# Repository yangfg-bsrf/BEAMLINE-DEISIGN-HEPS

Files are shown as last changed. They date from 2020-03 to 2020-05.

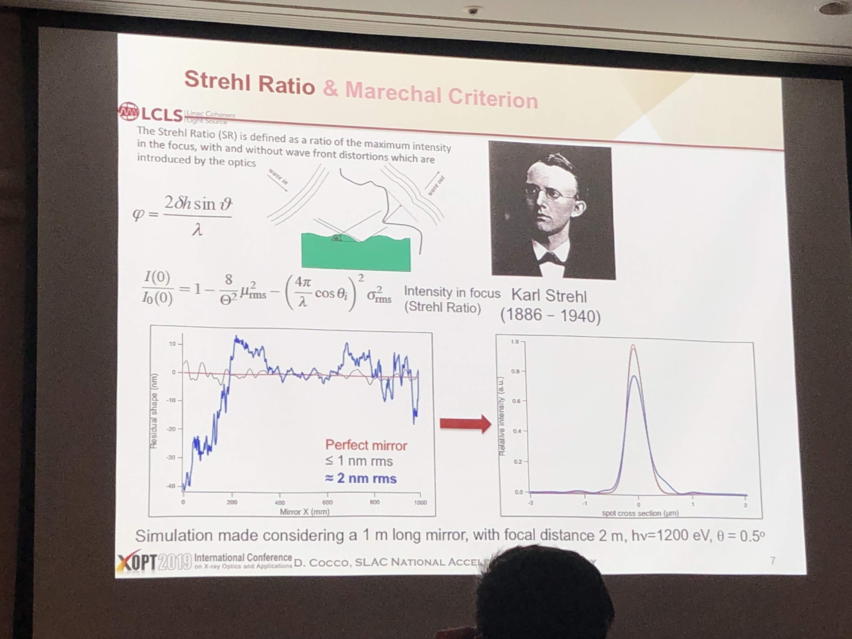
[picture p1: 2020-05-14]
report_discussion/反射镜面形误差2020-4-11/Coco/IMG_3269.JPG

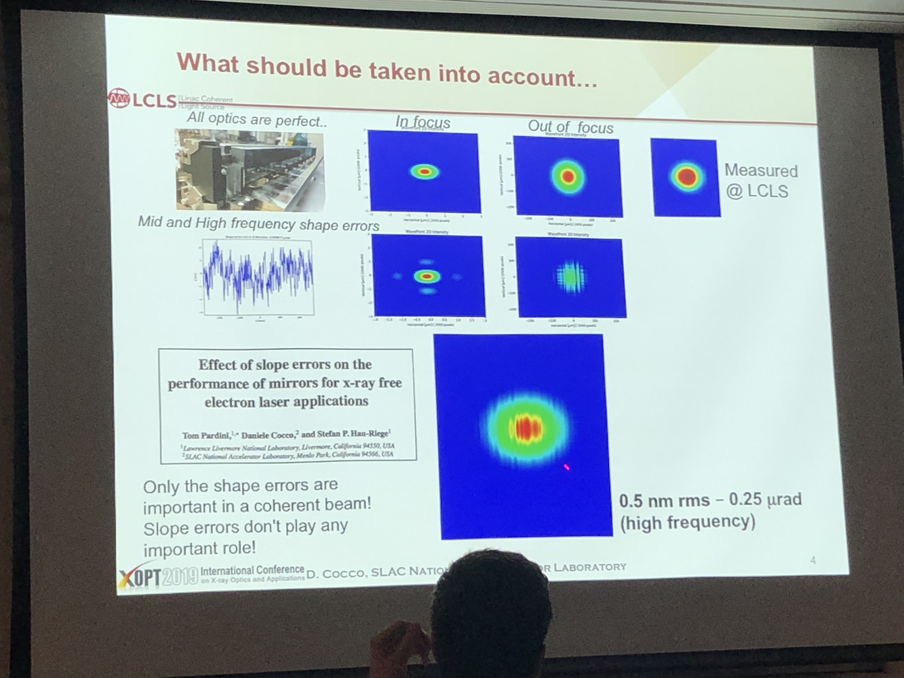
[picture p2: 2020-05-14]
report_discussion/反射镜面形误差2020-4-11/Coco/IMG_3266.JPG

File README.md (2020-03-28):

# BEAMLINE DEISIGN related simulation and study@HEPS

This work relates to the beamline design work in High Energy Photon Source project since 2018.

Different simulation software, including SRW, XRT, SHADOW-OUI, SHADOW-Hybrid, are used in the different beamline performance estimation. They give us big help in the beamline design research. We appreciate the software developer's contribution.

In this project, we will include some data\examples\problems for the people who want to do related work in HEPS.  

## how to design the beamline and simulation experiment

   (1) for specific issue, simulation and theoretical study are carried out and summarized;

   (2) for specific beamline, series of simulation and study are done

## how to program

   (1) Examples for HEPS beamlines

   (2) Examples for data_analysis

   (3) Codes for specific function, such as error generation(from Ansys, metrology), optical module with error, analysis module and so on

## other resources

   (1) HEPS parameters

   (2) Database for different kind of error

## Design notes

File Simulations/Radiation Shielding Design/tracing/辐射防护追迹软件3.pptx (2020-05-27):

## B8辐射防护追迹

- 2020-5-27

## 计算条件：

- 光源
- 白光狭缝位置35.3m
- CCM单色器位置40.8m，gap 7mm，高差12.7mm
- DCM单色器位置42.85m，高差19mm
- 准直器位置 （见图，纵坐标单位mm，横坐标单位m）
前端
束线

APS 7GeV 设计准则
L
3倍Moliere半径
铅：12~15mm，取50mm
钨：8~10mm，取35mm
t
20倍辐射长度
铅：5.6mm，取300mm
钨：3.5mm，取180mm
O
重叠6.5mm

## 做图示例说明

做图比例：88:1

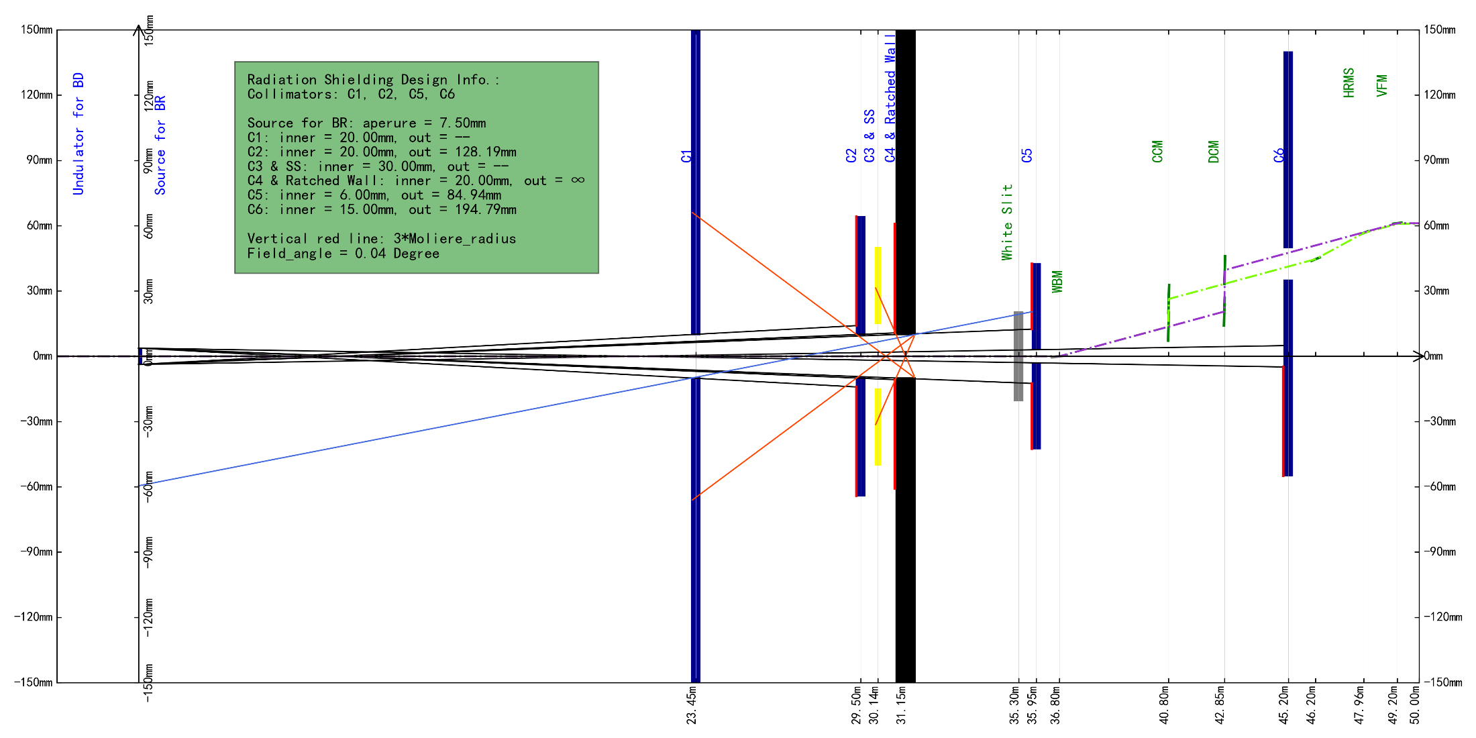
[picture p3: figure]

2. 画图比例：水平坐标m，竖直轴坐标mm
3. 各器件的位置，见对应的横纵坐标。如需光学器件的参数，后期可附

5. 器件名称：蓝色准直器件，绿色同步光学器件；全称见下。

1、包括准直器的内径，考虑3倍Moliere半径的外口径；经与石泓讨论，最终外口径可以按照10去整。

4. 光束线布局线，该束线有两个模式要考虑，因此有两条线。

器件全称名称：
White Slit:白光狭缝；WBM：白光镜；CCM：Channel-Cut晶体单色器；DCM：双晶单色器，HRMS：谐波抑制镜组；VFM：垂直聚焦镜

## B8辐射防护追迹1 -垂直方向：C5真空内 30mm

工况1
C5真空内，6mm；CCM gap =7mm, DCM offset =19mm; HRMs gap = 3mm

40.75mm
35mm
4.83mm

位置 内径 外径

C5: 35.95m, 6mm, 90mm
C6: 45.2m, 15mm, 200mm

## 水平方向

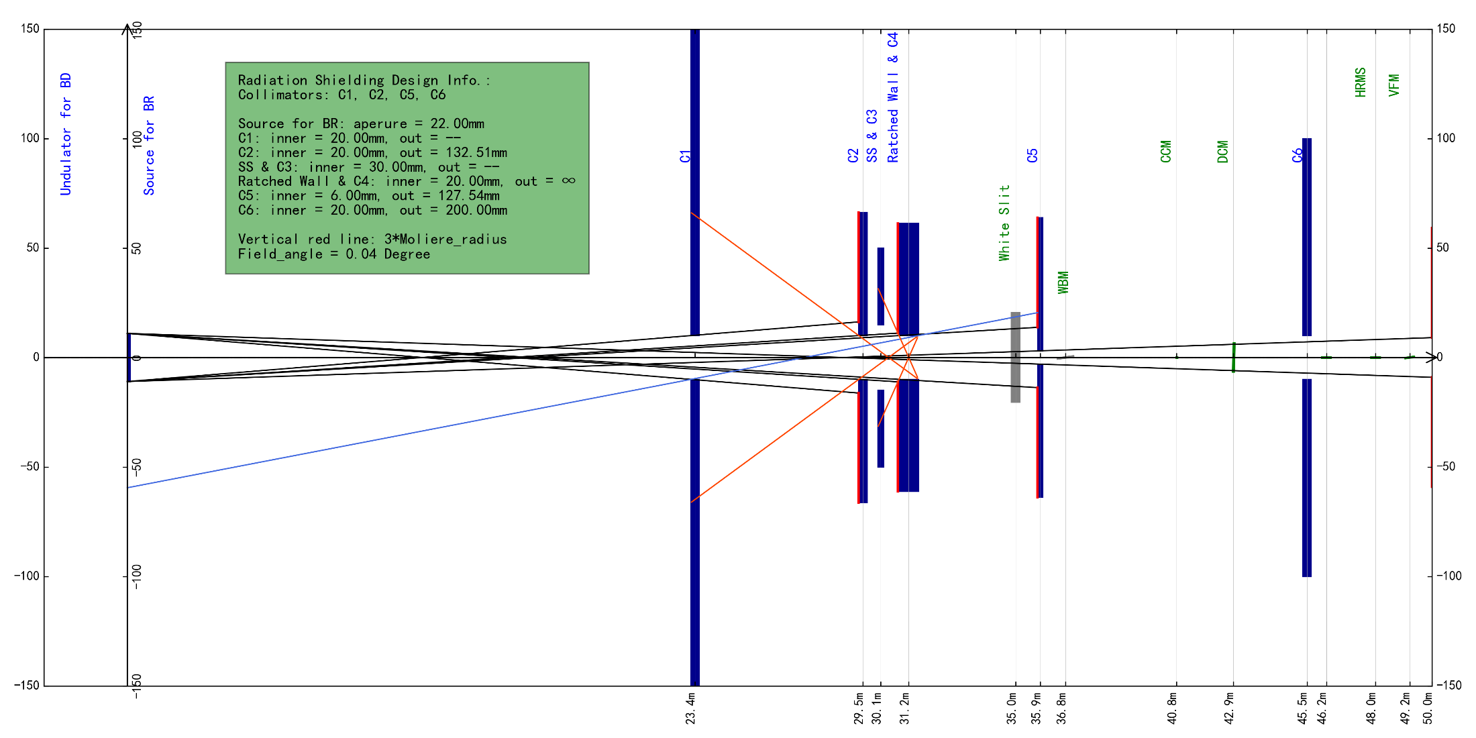
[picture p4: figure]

## B8辐射防护追迹2 -垂直方向 ；C5真空外 24mm

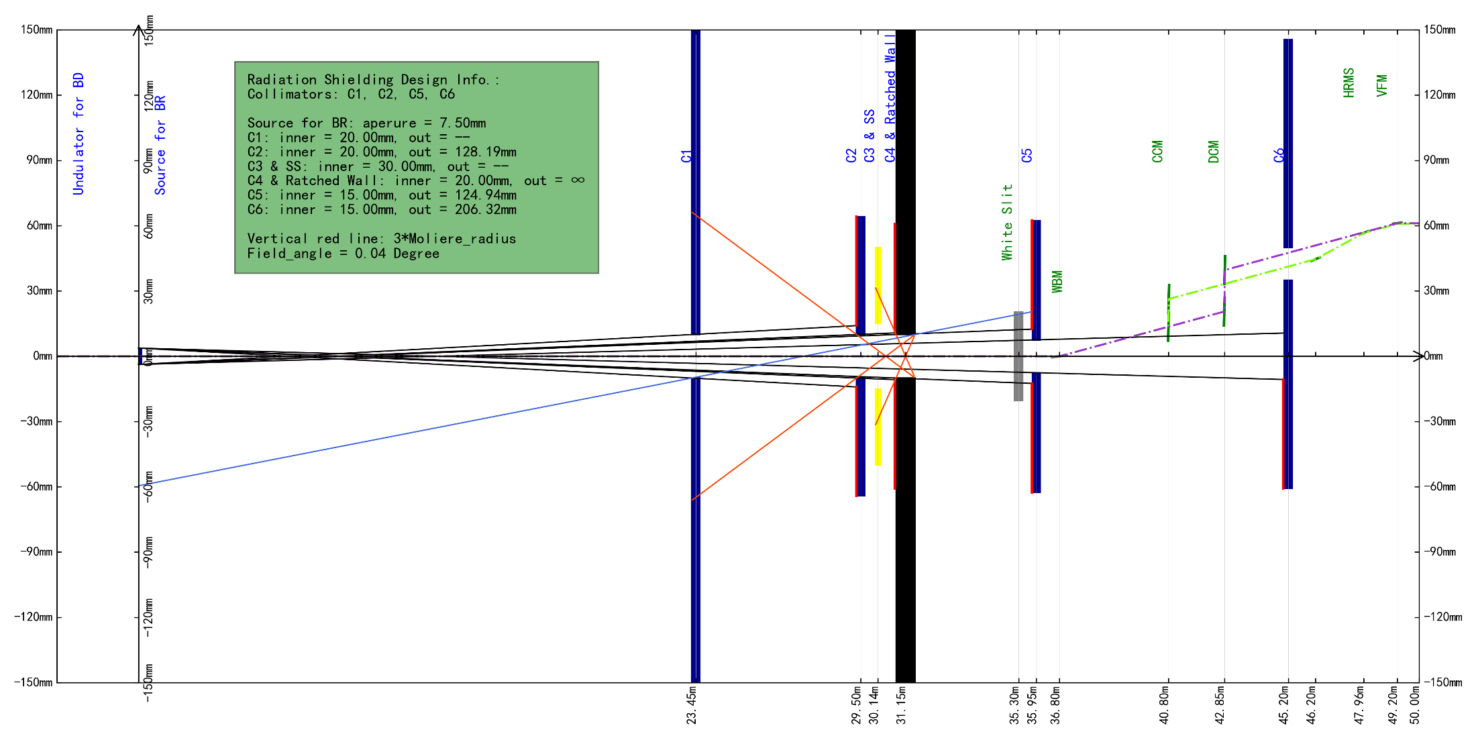
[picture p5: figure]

工况2
C5真空外，15mm；CCM gap =7mm, DCM offset =19mm; HRMs gap = 3mm

40.75mm
35mm

11mm

位置 内径 外径

C5: 35.95m, 15mm, 130mm
C6: 45.2m, 15mm, 210mm

## 水平方向

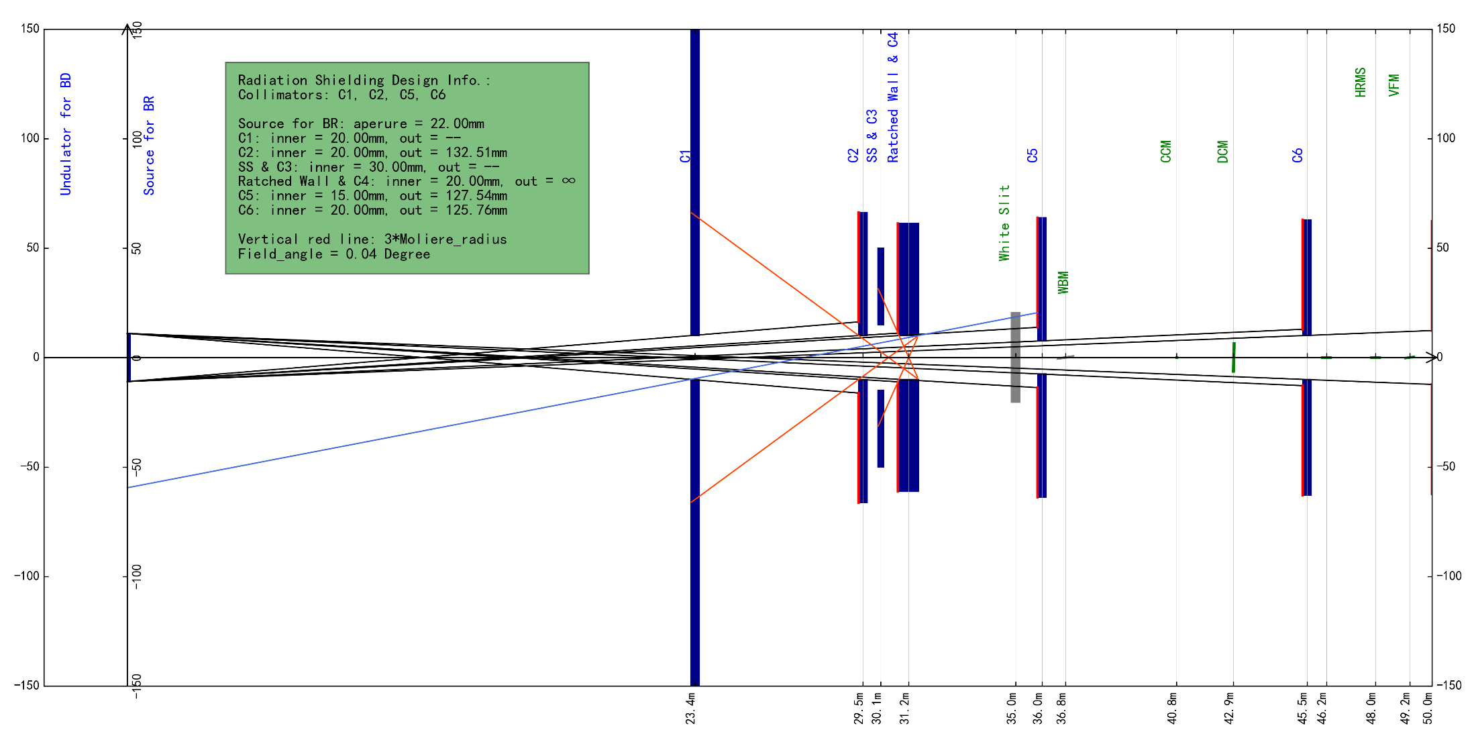
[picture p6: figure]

## B8辐射防护追迹3 -垂直方向；C5真空外后移 31mm

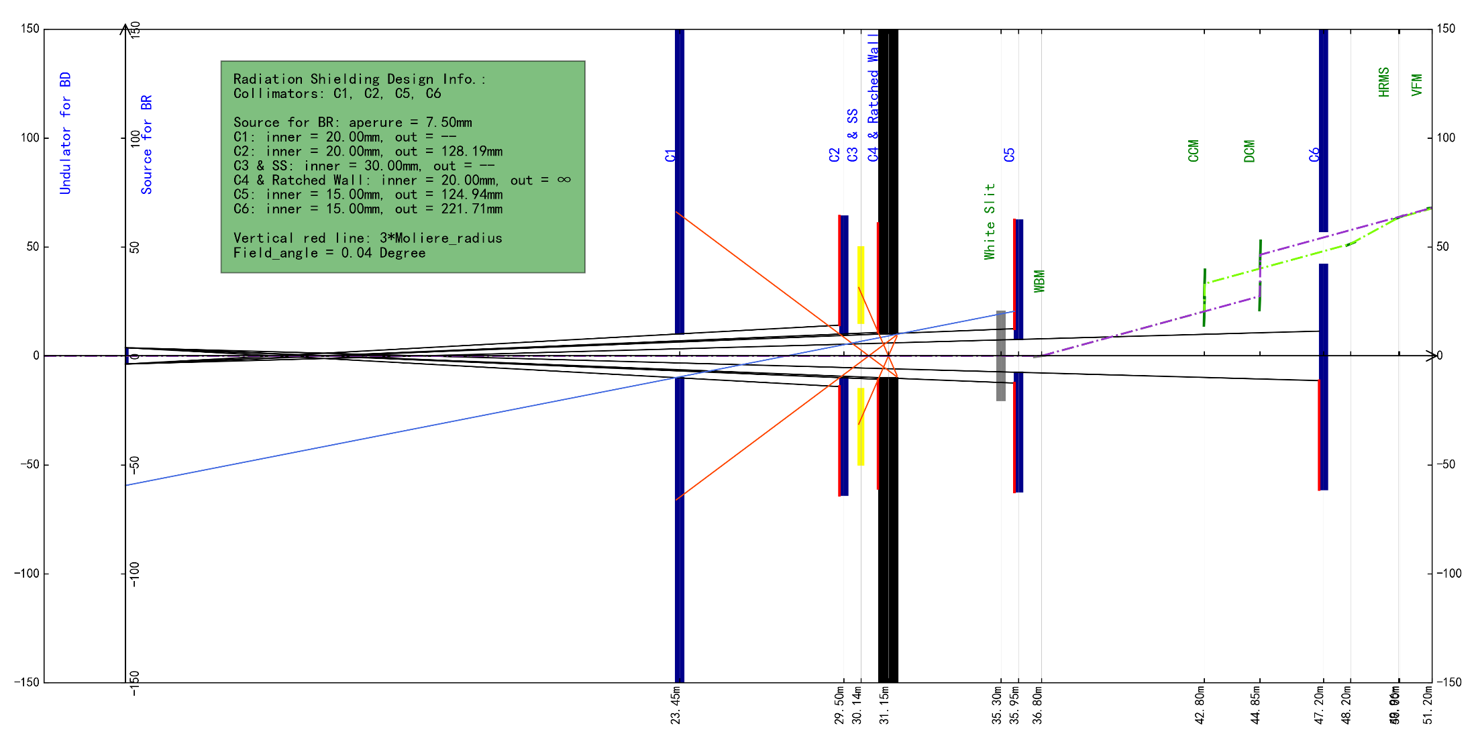
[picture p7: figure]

工况3
C5真空外，15mm；CCM gap =7mm, DCM offset =19mm; HRMs gap = 3mm；后移2m

47.2mm
42mm

11mm

位置 内径 外径

C5: 35.95m, 15mm, 130mm
C6: 47.2m, 15mm, 230mm

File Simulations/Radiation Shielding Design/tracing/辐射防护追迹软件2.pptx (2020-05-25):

## 辐射防护追迹软件

- 2020/5/25

## 3. 轫致辐射追迹画法

- 光源
  - 位置：
    - ID：直线节下游出口法兰端面
    - BM：弯铁中心（？）
  - 尺寸：
    - 真空盒内表面

- 准直器
  - 基本尺寸：
    - 上下游法兰端面间距：400mm
    - 厚度（t）：300mm（铅）或180mm（钨）
    - 外轮廓：依据BR追迹图（L=50（Pb）或35（W）mm）
    - 孔径余量：2~5mm
  - 位置
    - 最佳位置：单色器前
    - 必要位置：白光狭缝后
- Beamstop
  - 基本尺寸：同准直器
  - 位置：
    - 最佳位置：单色器后
    - 必要位置：FOE端墙前（或可以终止PBR的地方，例如白光束线实验hutch的端墙，建议尽可能接近样品）

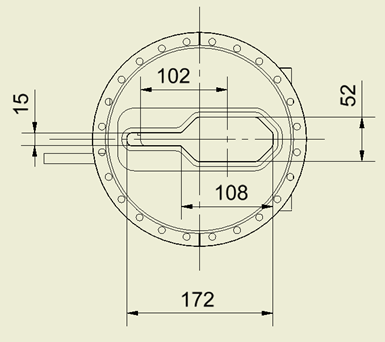
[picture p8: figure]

BEPC II 真空盒截面

## 追迹的思路

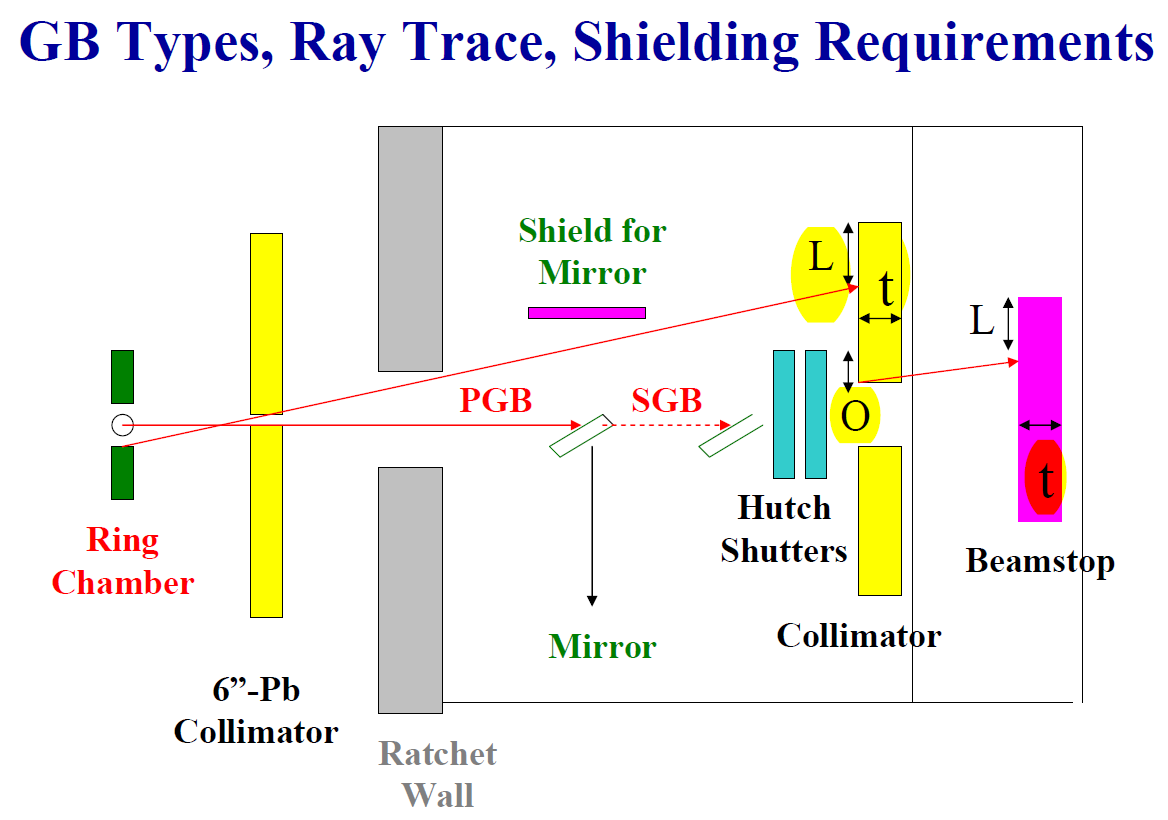
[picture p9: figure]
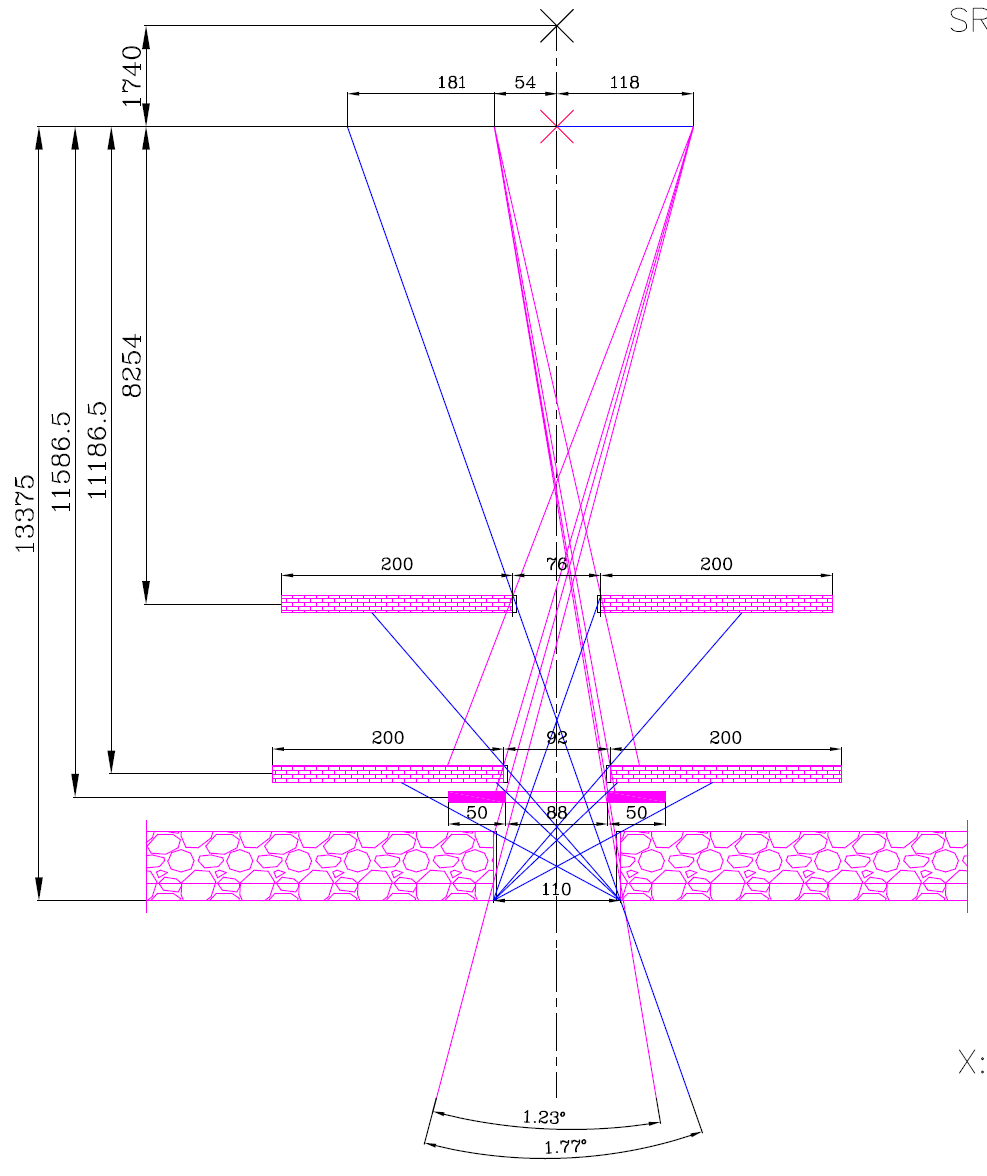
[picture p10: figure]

NEW：22mm * 7.5mm

器件类型：
光源（真空盒）
前准直器（前端）
锯齿墙

器件参数：
边缘坐标点位置，厚度t，高度h，宽度l

## B8辐射防护追迹1

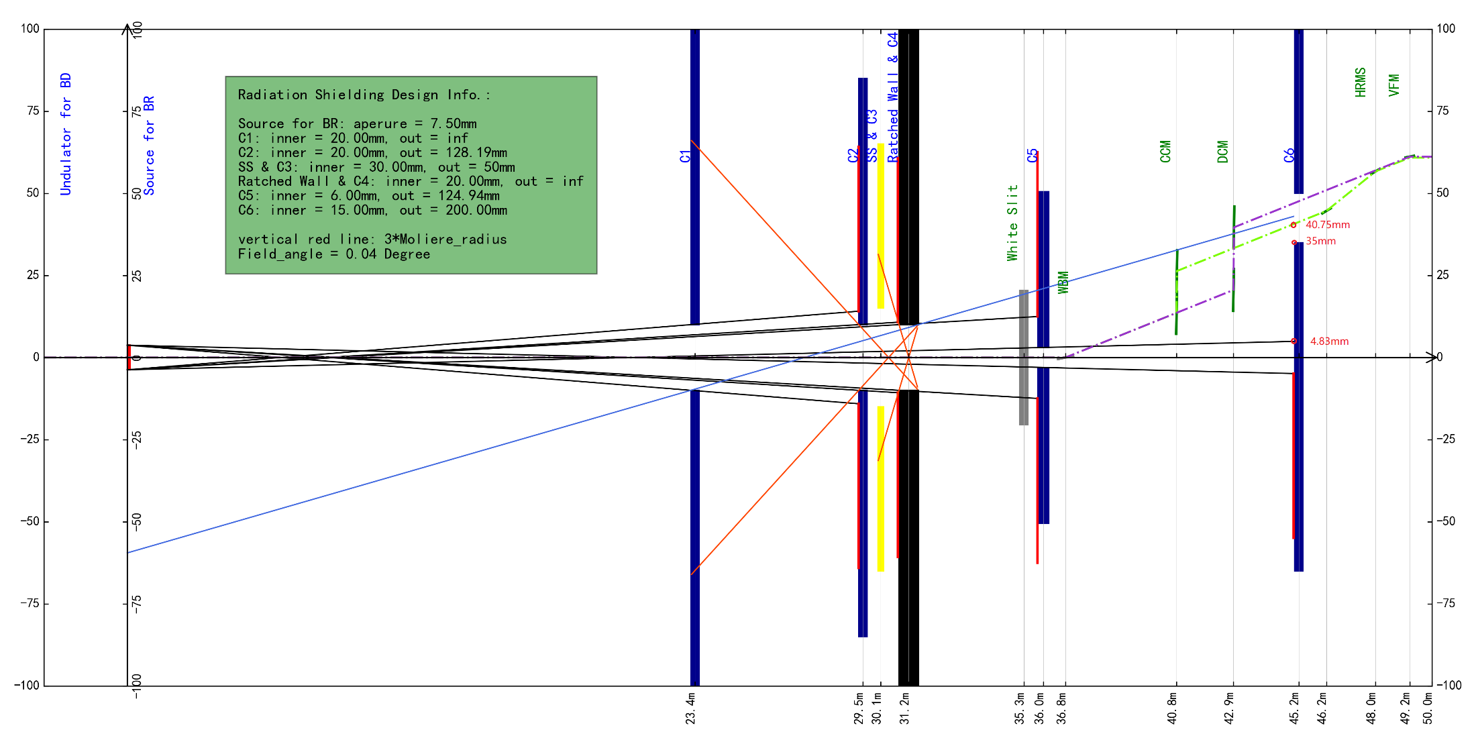
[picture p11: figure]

工况1
C5真空内，6mm；CCM gap =7mm, DCM offset =19mm; HRMs gap = 3mm

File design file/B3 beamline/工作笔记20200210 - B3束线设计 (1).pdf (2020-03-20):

# HEPS 工程工作笔记

## HEPS Technical Note

标题（Title） | B3 束线设计 – 波动计算
作者 (Author)/ 系统 (System) | 杨福桂 | 日期 (Date) | 2020-2-10
编号 (Serial No.) | | 页数 (Pages) | 共 页 (含附件)

摘要 (abstract)：

B3 结构动力学线站的光束线设计方案已基本确定，即采用两级 CRL 聚焦实现微米聚焦，

CRL-多层膜聚焦镜实现纳米聚焦。考虑到 HEPS 的相干性，需要开展部分相干的计算，这里

结合 SRW 和 XRT 两个软件。本工作主要是评估：粉光（宽带宽）和 CRL 面形误差特征下，

部分相干性对束线微米聚焦性能。

从仿真结果来看，在当前仿真设置下，光源尺寸和色差是影响聚焦性能的主因，部分相

干性的影响较小。

会 签 Concurred by

有效性 Validation | 填表人 Prepared by | 审 核 Reviewed by | 批 准 Approved by
签 名 Signature | XX
日期 Date | XX（一定写上日期）

### 1 束线光学设计综述

### 1.1 光源特征

HEPS-B3 分别处于低和高 beta 直线节。储存环和光源参数如表格 1 1 所示。

| HEPS-B3
电子能量 (GeV) | 6
电流强度 (GeV) | 0.2
能散 | 0.00111
电子尺寸 (μm) | 8.8*2.3
电子束团发散角 (μrad) | 3.1*1.2
Beta function | 2.84*1.92
发射度 (pm*rad) | 27.28*2.76
能量点@谐波级次 | 23keV@1st
λ/2π (pm.rad) | 19.74
周期 (mm) | 12
周期数 | 180
表格 1-1 光源参数列表

### 1.2 束线布局

由于光源处发光点的位置非确定，因此这里需要从波动计算结果分析光源尺寸。仿真束 线布局图如图 1-1 所示。B3 采用级联聚焦的方式，前级聚焦 CRL 的曲率半径为 0.5mm， 组数为 11 个；后级聚焦 CRL-2 的曲率半径为 0.05mm，片数为 6。白光狭缝尺寸为 15urad 接收角，对应边长为 0.6mm 的方形狭缝。在 CRL1 前后各放一个限光圆形狭缝，直径 0.8mm；CRL2 前后各方一个限光狭缝，狭缝直径为 0.4mm。

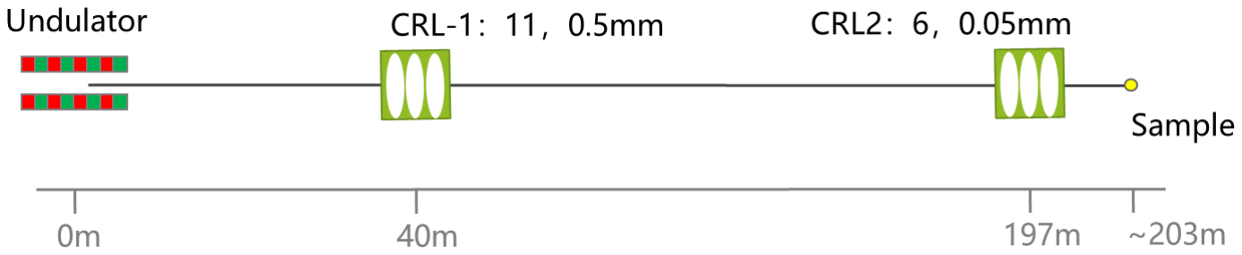
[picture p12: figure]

图 1-1 仿真布局图

### 2 聚焦位置的确定

CRL 的有限厚度以及误差都会引起焦点位置的移动，焦点位置的确定变成一个有别于反 射镜的重要工作。从下面的计算，我们还能发现，确定焦平面位置也是需要讨论的内容。 为了便于分解各种因素的影响，这里计算了面形误差、光源尺寸以及带宽的影响。

### 2.1 面形误差的影响

考虑到面形误差主要来源是由小曲率半径 CRL 组成的 CRL-2，在本文的计算中，CRL-1 不加载面形误差。

### 2.1.1 无误差-单色情况

设置光源 0.0001%带宽，开展光线追迹和波动传播计算。其中，在波动计算中使用单
电子发光。计算结果如(e) | (f)
图 2-1 和图 2-2 所示。由于几何追迹情况下，样品处的光斑尺寸是多电子发光的尺寸， 因此(e)图的尺寸有很大的不同。

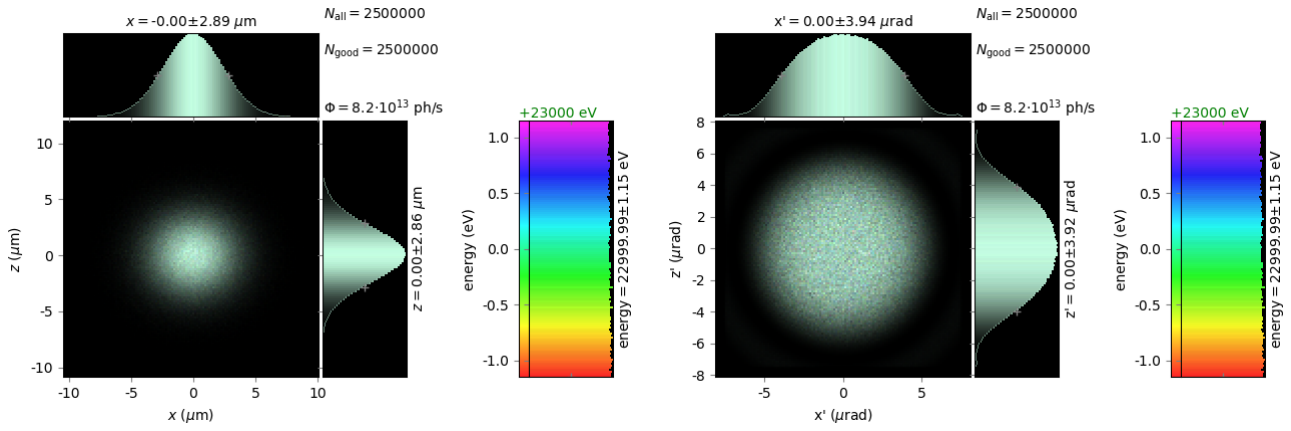
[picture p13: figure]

(a) (b)

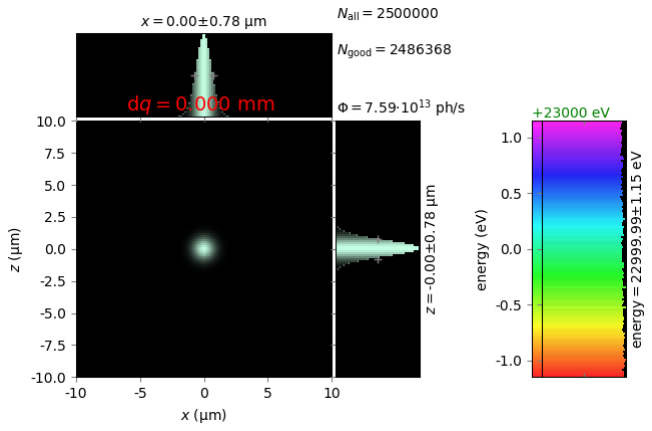
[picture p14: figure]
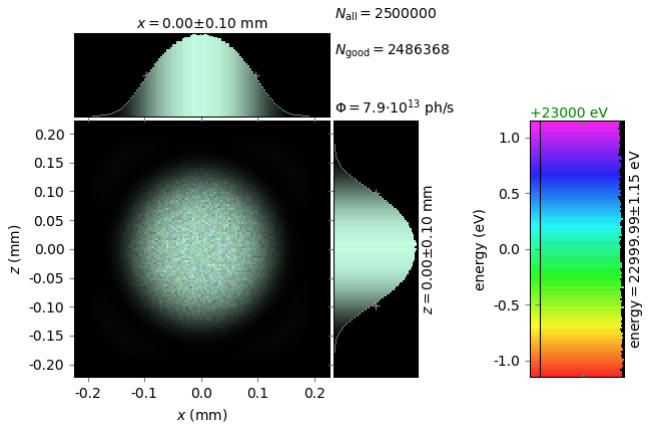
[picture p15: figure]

(c) (d)

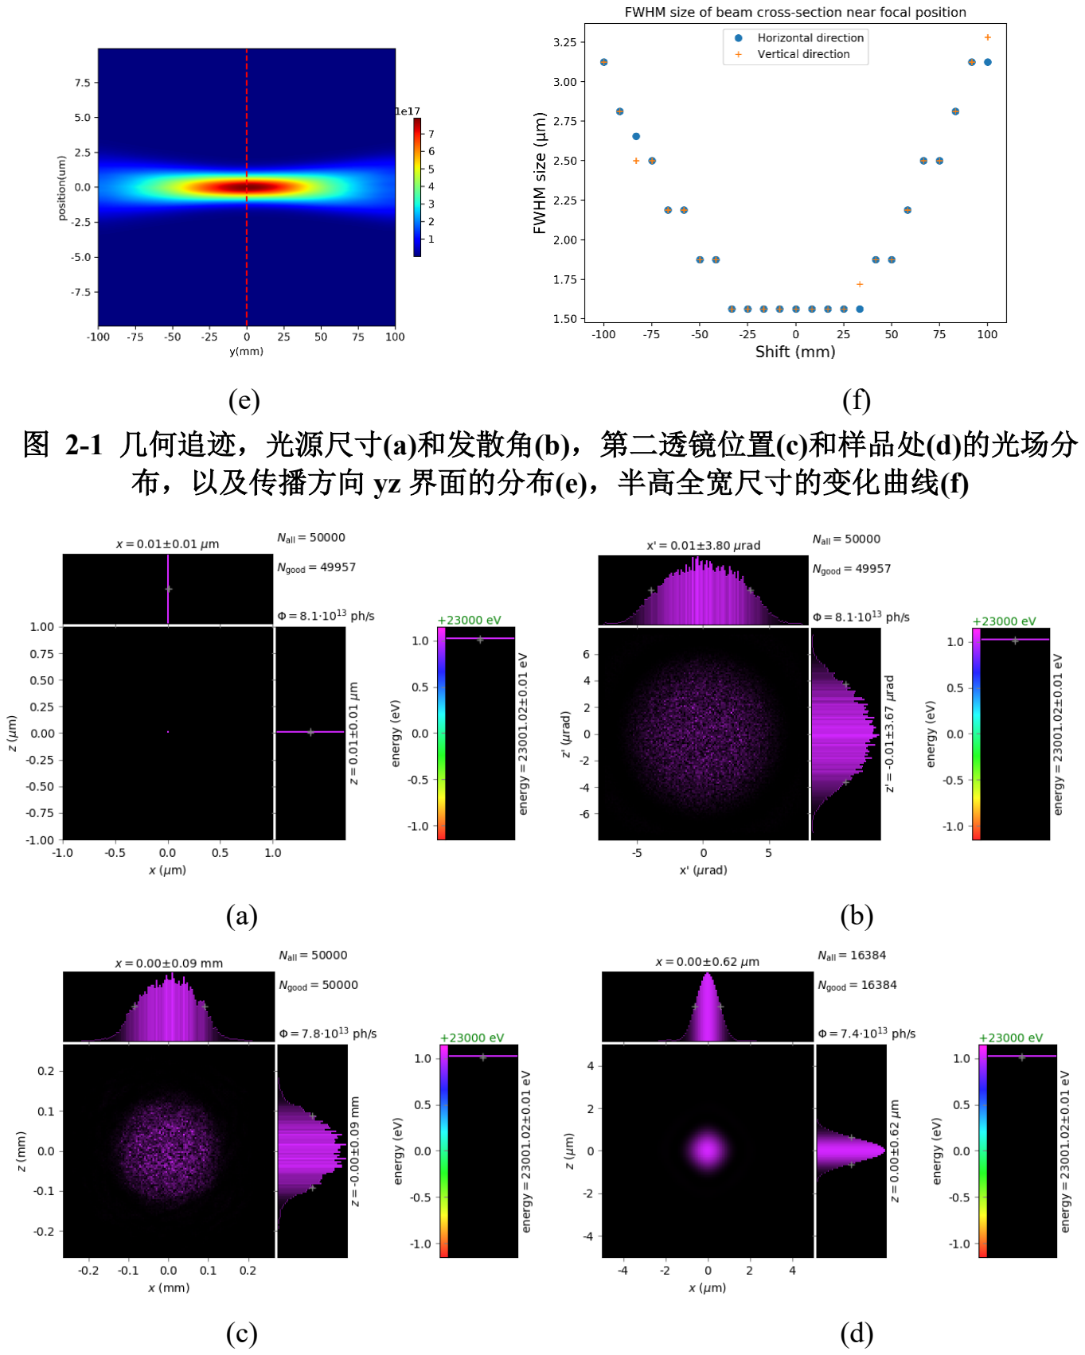
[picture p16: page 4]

(e) (f)
图 2-1 几何追迹，光源尺寸(a)和发散角(b)，第二透镜位置(c)和样品处(d)的光场分 布，以及传播方向 yz 界面的分布(e)，半高全宽尺寸的变化曲线(f)
(a) (b)
(c) (d)

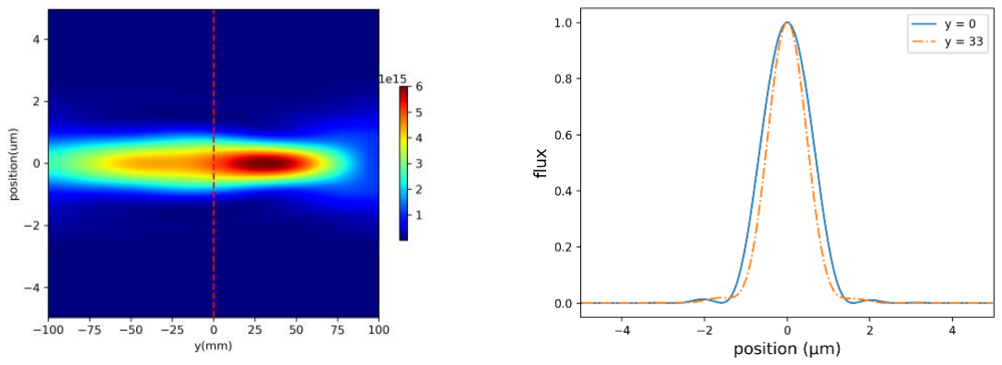
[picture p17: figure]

(e) (f)

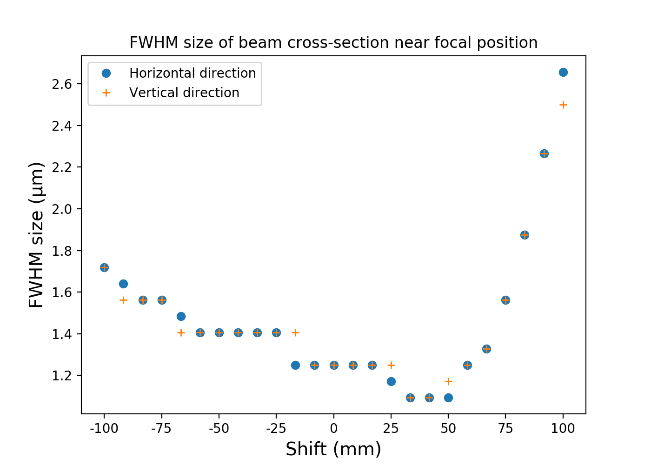
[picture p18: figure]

(g)
图 2-2 波动传播，光源尺寸(a)和发散角(b)，第二透镜位置(c)和样品处(d)的光场分 布，以及传播方向 yz 界面的分布(e)，y=0 和 33mm 处的一维曲线(f)，半高全宽尺寸的 变化曲线(g)

几何追迹结果和波动计算结果均显示最小光斑位置大致在 20-50mm 之间。从图 2-2(f)曲线看出，理想成像的焦点应该在 0mm 处，此处的波形体现的振荡特征与光源相 近。但在 y=33mm 处光斑尺寸是最小的。
进一步地，使用 SRW 开展单电子波动追迹。截面分布与 XRT 单电子波动计算结果 一致。SRW 中的透镜焦距为 6.47 m，由于 B3 前级为准直，因此基本最小光斑位置在焦 点位置附近。

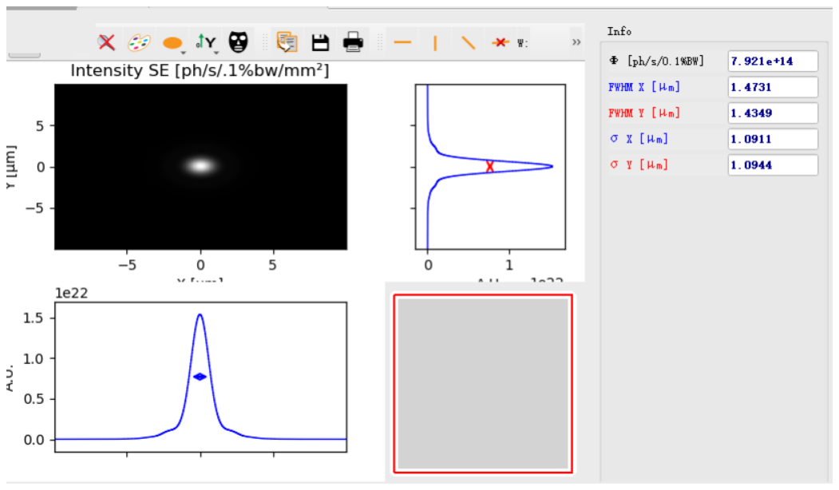
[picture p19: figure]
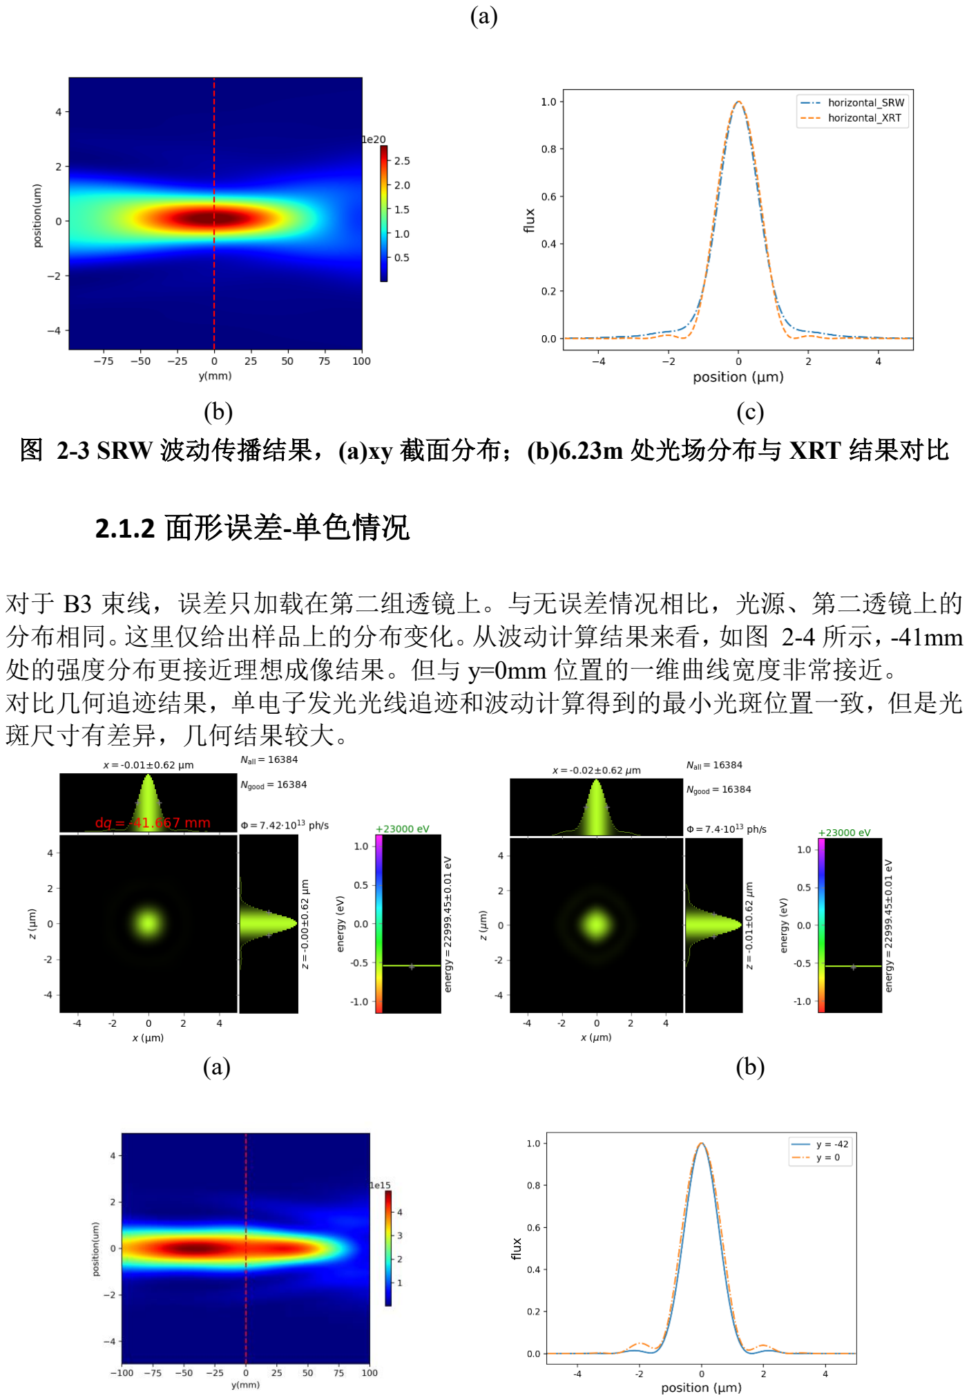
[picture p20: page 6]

(a)

(b) (c)
图 2-3 SRW 波动传播结果，(a)xy 截面分布；(b)6.23m 处光场分布与 XRT 结果对比

### 2.1.2 面形误差-单色情况

对于 B3 束线，误差只加载在第二组透镜上。与无误差情况相比，光源、第二透镜上的 分布相同。这里仅给出样品上的分布变化。从波动计算结果来看，如图 2-4 所示，-41mm 处的强度分布更接近理想成像结果。但与 y=0mm 位置的一维曲线宽度非常接近。 对比几何追迹结果，单电子发光光线追迹和波动计算得到的最小光斑位置一致，但是光 斑尺寸有差异，几何结果较大。

(a) (b)

(c) (d)

(e)
图 2-4 波动传播，y=0 和 33mm 处的的光场分布(a) (b)，以及传播方向 yz 界面的分布 (c),y=0 和 33mm 处的一维曲线(d) ，半高全宽尺寸的变化曲线(e)
(a) (b)
(c) (d)
图 2-5 几何追迹，y=-41.6mm 和 0mm 处的的光场分布(a) (b)，以及传播方向 yz 界面 的分布(e)，光斑半高全宽尺寸的变化曲线(d)

### 2.2 光源尺寸的影响

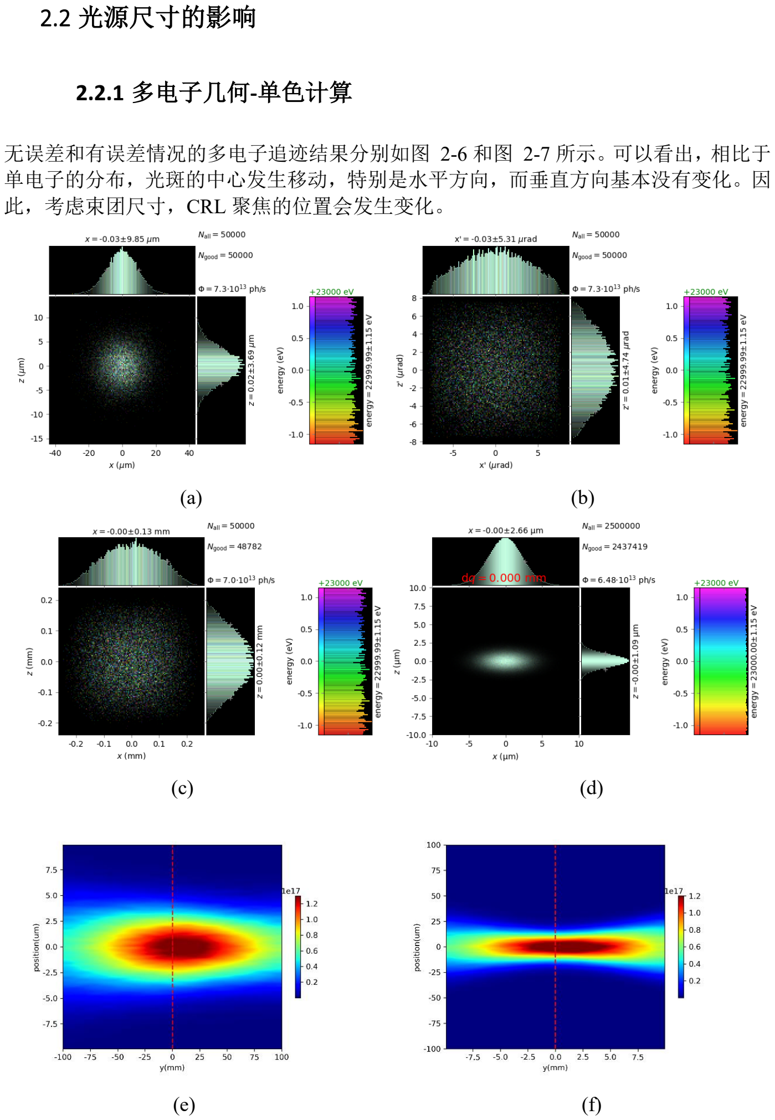
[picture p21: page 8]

### 2.2.1 多电子几何-单色计算

无误差和有误差情况的多电子追迹结果分别如图 2-6 和图 2-7 所示。可以看出，相比于 单电子的分布，光斑的中心发生移动，特别是水平方向，而垂直方向基本没有变化。因 此，考虑束团尺寸，CRL 聚焦的位置会发生变化。

(a) (b)
(c) (d)
(e) (f)

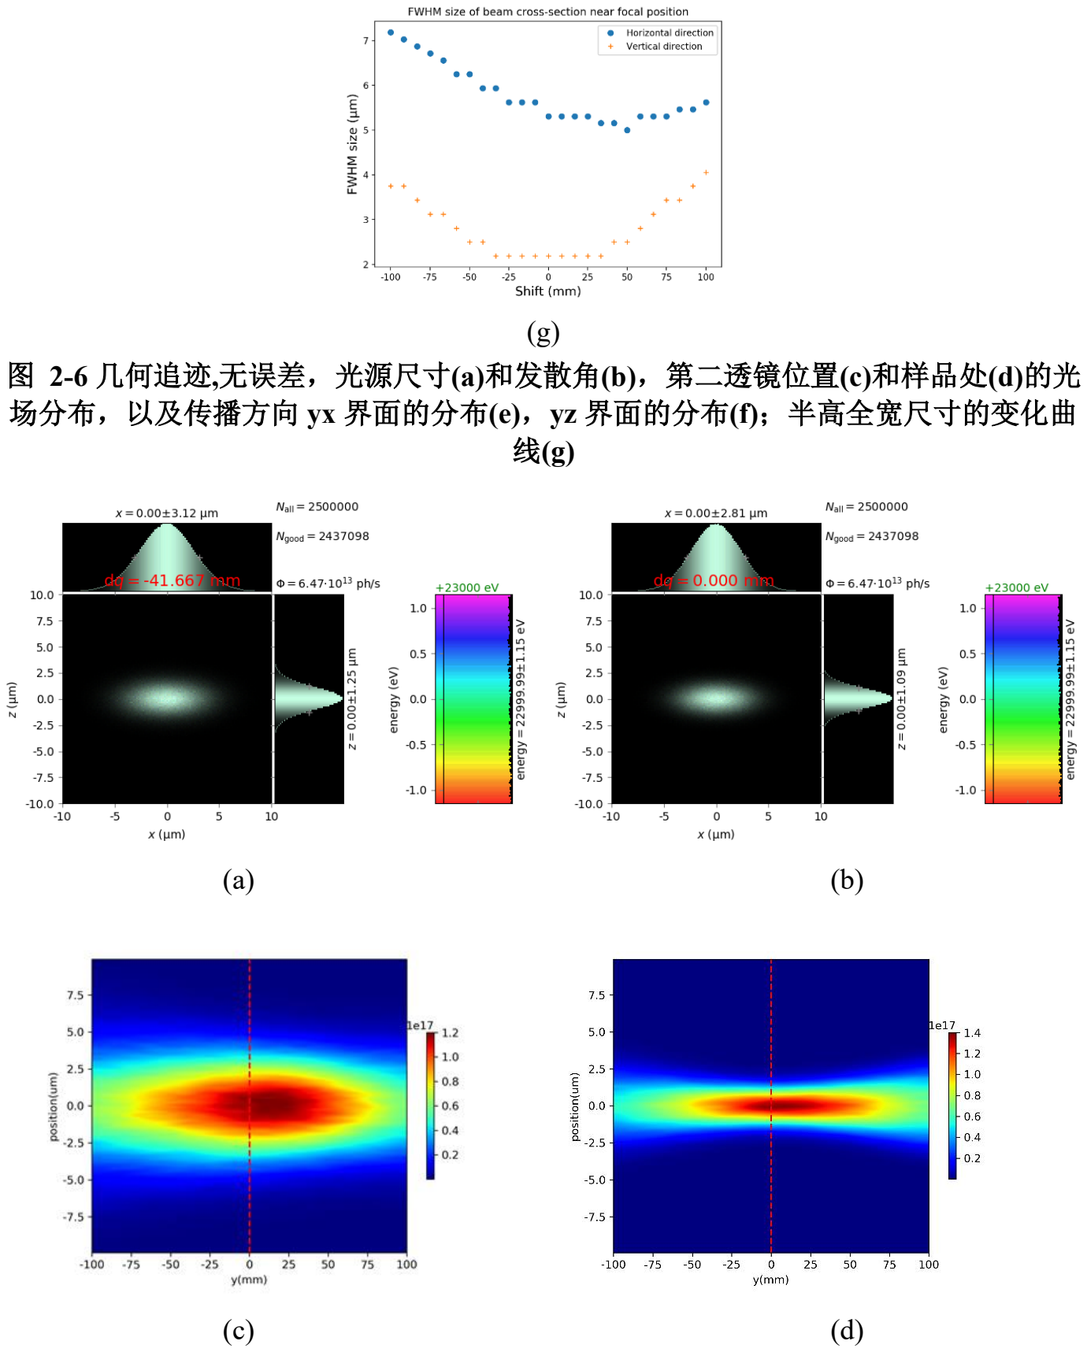
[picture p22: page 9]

(g)
图 2-6 几何追迹,无误差，光源尺寸(a)和发散角(b)，第二透镜位置(c)和样品处(d)的光 场分布，以及传播方向 yx 界面的分布(e)，yz 界面的分布(f)；半高全宽尺寸的变化曲 线(g)
(a) (b)
(c) (d)

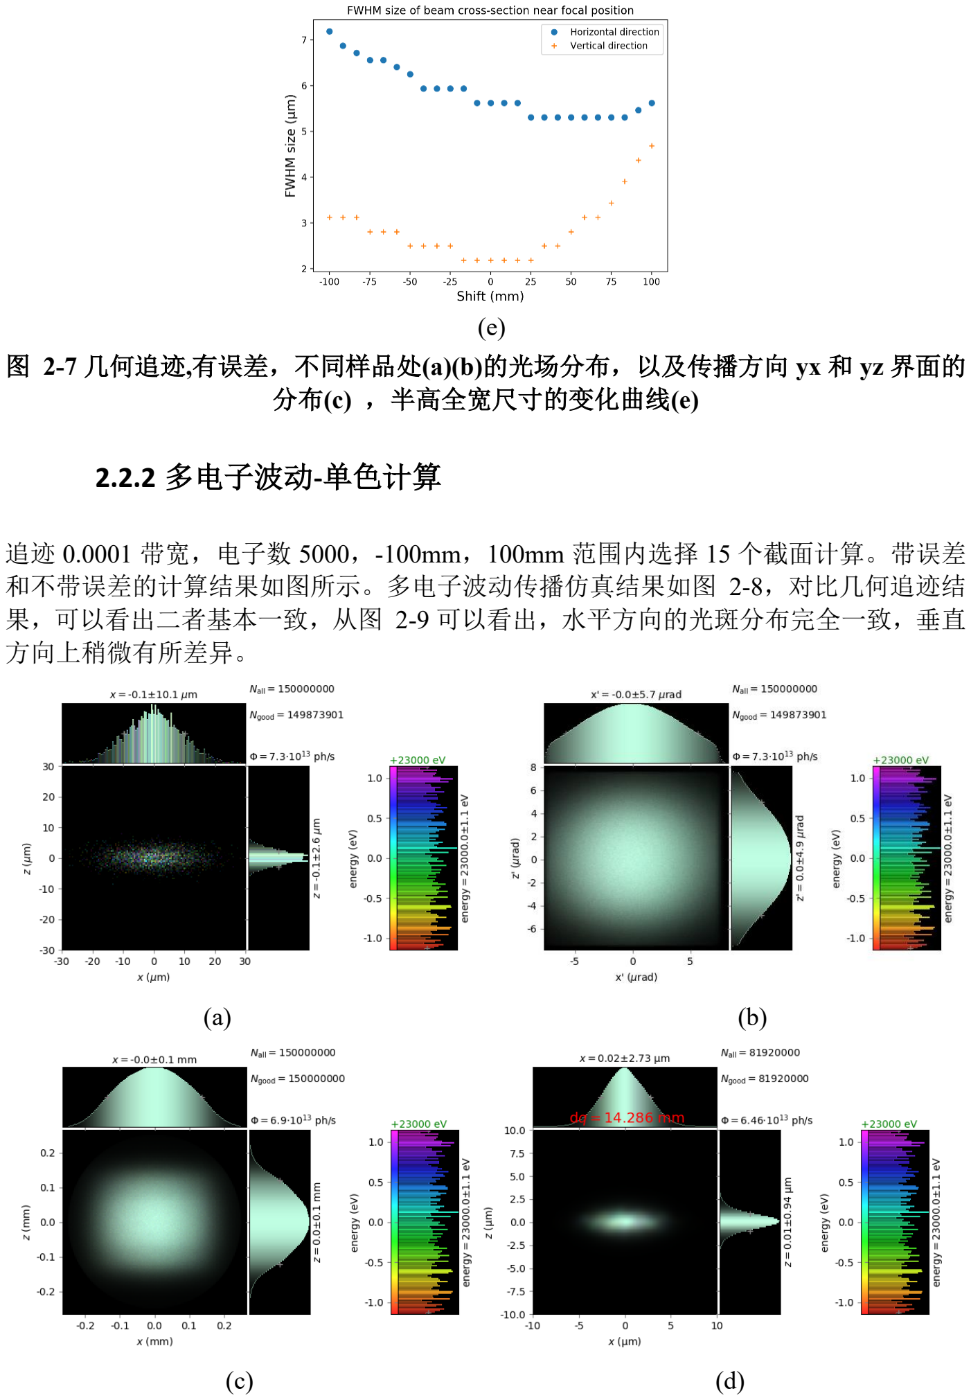
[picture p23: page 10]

(e)
图 2-7 几何追迹,有误差，不同样品处(a)(b)的光场分布，以及传播方向 yx 和 yz 界面的 分布(c) ，半高全宽尺寸的变化曲线(e)

### 2.2.2 多电子波动-单色计算

追迹 0.0001 带宽，电子数 5000，-100mm，100mm 范围内选择 15 个截面计算。带误差 和不带误差的计算结果如图所示。多电子波动传播仿真结果如图 2-8，对比几何追迹结 果，可以看出二者基本一致，从图 2-9 可以看出，水平方向的光斑分布完全一致，垂直 方向上稍微有所差异。

(a) (b)
(c) (d)

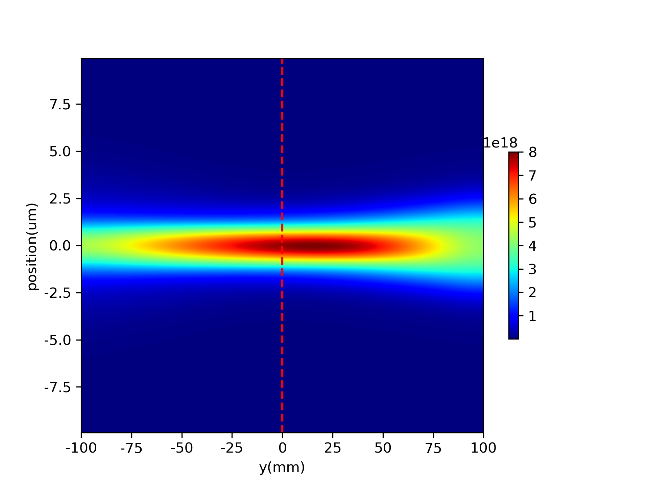
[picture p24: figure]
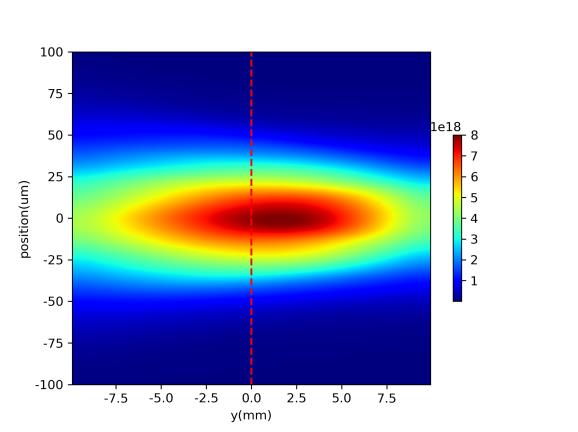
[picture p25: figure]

(e) (f)

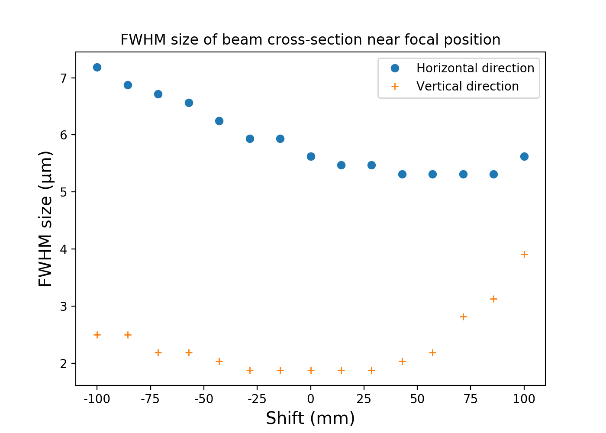
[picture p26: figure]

(g)
图 2-8 多电子波动传播，带误差，光源电子尺寸(a)和光场发散角(b)，第二透镜位置(c) 和样品处(d)的光场分布，以及传播方向 yx 界面的分布(e)，yz 界面的分布(f)；半高全 宽尺寸的变化曲线(g)


图 2-9 几何追迹与波动传播结果对比

### 2.3 色散的影响

### 2.3.1 几何追迹情况

考虑有误差和无误差，在近 0.03 带宽下的分布如图 2-10 和图 2-11。系统接收口径下， 对应的带宽为 0.0107。该带宽在系统传输过程中，能够完全被系统传输，从图 2-10(c)可 以看出蓝色的高能量光线在第二组透镜上的聚焦光斑更小，而低能量的光线扩展至 0.36mm，仍在第二透镜的口径范围内。


(a) (b)


(c)
图 2-10 光线追迹结果，光源(a)(b)与 CRL-2 前的光场分布(c)


(a) (b)
(c) (d)
(e) (f)


(g) (h)
图 2-11 光线追迹结果，(a)(c)(e)误差，(b)(d)(f)有误差

### 2.3.2 多电子波动传播情况

这里仅追迹带有误差的情况，如图 2-12 所示，对比 2.3.1 节的几何追迹结果，二者接近： 包括最佳成像位置的移动，光斑半高全款尺寸等。这说明，由于色差的存在，几何光线 追迹结果已经可以做出很好地近似，说明大致的问题。从像差的角度来说，由于色差问 题比较严重，此时可以认为是非相干情况来处理。虽然多电子波动传播可以给出更准确 的计算结果，缺点是耗时。将-85.7m 的中心位置光场分布一维曲线做在同一幅图中，如 图 2-13 所示。


(a) (b)


(c) (d)
图 2-12 多电子波动追迹结果，yx 和 yz 截面图(a)(b)，CRL-2 入射光场分布，以及各 个位置的光斑尺寸。
(a) (b)

(c)
图 2-13 -87.5mm 处的光场分布，二维分布(a)(b)和一维分布曲线(c)

### 3 总结

第一，对于当前的束线，误差的影响很小可以忽略。
第二，当带宽比较窄时，由于光斑尺寸的扩展效应，波动传播和几何追迹结果一致。 第三，当带宽非常宽时，由于色散效应，光场的分布会发生变化，例如焦点位置的前移 等。几何追迹结果可以很好近似波动传播。

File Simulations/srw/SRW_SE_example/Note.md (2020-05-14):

## 如何使用SRW？核心是函数库的安装，及编程方式

### 1. 直接安装SRW python

   <https://srwpy.github.io/srwpy/index.html>
   <https://github.com/srwpy/srwpy>

    安装：pip install srwpy

    *使用*：
     >from srwpy.srwlib import *
     >from srwpy.uti_plot import *

### 2. 库文件调用

   <https://github.com/ochubar/SRW>

    参照本文件夹下的SRW_SE_example

    *使用*：
    > from srwlib import *
    > from uti_plot import *

### 3. 使用OASYS_SRW生成代码，运行程序

<https://www.aps.anl.gov/Science/Scientific-Software/OASYS>
   
    *使用*：
    > from oasys_srw.srwlib import *
    > from oasys_srw.uti_plot import *

### 4. 使用Sirepo生成代码

 <https://www.bnl.gov/ps/groups/rd/simulations/tools.php>

 <https://www.sirepo.com/light#/home>

 <https://github.com/radiasoft/sirepo>

    *使用*：
    > import srwl_bl
    > import srwlib
    > import srwlpy

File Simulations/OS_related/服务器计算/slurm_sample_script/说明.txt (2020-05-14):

slurm_cpu.sh
sacct
scancel

source /afs/ihep.ac.cn/users/z/zhaohf/.bash_profile
����Ŀ¼
/afs/ihep.ac.cn/users/y/yangfg
��ҵ�ύĿ¼
/workfs/heps/yangfg
CPU�洢Ŀ¼
/scratchfs/heps/yangfg
GPU�洢Ŀ¼
/hpcfs/heps/bldesign/yangfg

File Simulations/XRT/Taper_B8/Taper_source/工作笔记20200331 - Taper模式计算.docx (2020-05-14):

HEPS工程工作笔记

HEPS Technical Note

标题（Title） | | B8束线Taper模式相关计算
作者 (Author)/ 系统 (System) | | 杨福桂 | | 日期 (Date) | 2020-3-25
编号 (Serial No.) | | | | 页数 (Pages) | 共 页 (含附件)

摘要 (abstract)：

Taper模式是谱学束线的共同需求，针对HEPS的B8束线，开展Taper模式下插入件相关参数的设计与束线性能的计算。

结论：

[1]. 从对比

会 签 Concurred by
有效性Validation | 填表人 Prepared by | | 审 核 Reviewed by | | | 批 准 Approved by
签 名 Signature | XX
日期 Date | XX（一定写上日期）

# 1 B8束线的仿真参数

束线要求1keV的能量带宽。改变taper量，观察计算结果。

# 2 SPETRA和XRT仿真结果比对

## 2.1 介绍材料

关于Taper模式的计算，XRT对比了XRT、YAUP、SPECTRA三个软件以及实验测试的结果对比，如图 2-1所示，这种差异是可以接受的，毕竟常规实验的gap和taper并不是那么可靠。另一方面，各个软件中的taper定义也有所差别。“The gap values and the taper were slightly varied in all three codes to reach the best match with the experimental curve. We had to do so because in the other codes taper is not clearly defined (where is the gap invariant – at the center or at one of the ends?) and also because the nominal experimental gap and taper are not fully trustful.”


图 2-1 参考实例的比对结果

[1]. B. I. Boyanov, G. Bunker, J. M. Lee, and T. I. Morrison, Numerical Modeling of Tapered Undulators, Nucl. Instr. Meth. A339 (1994) 596-603.
[2]. T. Tanaka and H. Kitamura, SPECTRA - a synchrotron radiation calculation code, J. Synchrotron Radiation 8 (2001) 1221-8.
[3]. Measured on 27 Nov 2013 on P06 beamline at Petra 3, R. Chernikov and O. Müller, unpublished.

进一步地，为了保证XRT计算结果的正确性，这里对比了SPECTRA和XRT的计算结果。从图 2-2可以看到，XRT的曲线形状与SPECTRA基本一致，但是在幅度上有差异。


(a) (b)

图 2-2 一定口径内通量的频谱分布结果比对

更进一步地，考虑通量分布，图 2-1给出了几个能量点的空间分布对，可以看出，二者的分布基本一致。在光斑的空间分布上，角空间分布出现了明显得空间不均匀性。变化幅度在50%以下。


图 2-3 不同能量点对应的通量分布，左图和右图分别对应XRT和SPECTRA

# 3 理论推导

考虑如图 2-1的布局，反射镜的掠入射角为θ，下面将从基本旋转公式推导。


图 3-1 KB镜的布局参数

## 3.1 角度方向信息

基本依据是：对于特定的反射面，表面反射的入射波矢 t_(in) 和出射波矢 t_(out) 之间满足关系

t_(out) =t_(in) -2(t_(in) ∙n)n

其中， n 是反射面的法向矢量。

### 3.1.1 确定反射镜的旋转矩阵

以VKB为例，绕各轴的旋转矩阵表示为

T_(vkb,x) =[1, 0, 00, cosα_(vkb) , sinα_(vkb) 0, -sinα_(vkb) , cosα_(vkb) ] ， T_(vkb,y) =[cosβ_(vkb) , 0, sinβ_(vkb) 0, 1, 0-sinβ_(vkb) , 0, cosβ_(vkb) ] ，

T_(vkb,z) =[cosγ_(vkb) , sinγ_(vkb) , 0-sinγ_(vkb) , cosγ_(vkb) , 00, 0, 1]

按照XRT软件的设置，旋转顺序为RyRzRx，总得旋转量为

T_(vkb,total) =T_(vkb,x) T_(vkb,z) T_(vkb,y)

对于VKB， α_(vkb) =θ ， β_(vkb) =0 ， γ_(vkb) =0 ， T_(vkb,total) =T_(vkb,x) =[1, 0, 00, Cos[θ], -Sin[θ]0, Sin[θ], Cos[θ]]

对于HKB， α_(hkb) =2θ ， β_(hkb) =-π/2 ， γ_(hkb) =θ ，

T_(hkb,total) =T_(hkb,x) T_(hkb,z) T_(hkb,y)

=[0, -Sin[θ], -Cos[θ]-Sin[2θ], Cos[θ]Cos[2θ], -Cos[2θ]Sin[θ]Cos[2θ], Cos[θ]Sin[2θ], -2Cos[θ]Sin[θ]^2 ]

### 3.1.2 确定反射镜的法向量

反射镜的初始法向量均为

n_(initial) =[0, 1, 0]

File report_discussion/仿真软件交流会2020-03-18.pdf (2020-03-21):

High Energy Photon Source

# 软件仿真交流会

2020/3/20

HEPS @ IHEP | 2
- 背景

### ■ 软件交流

### ■ 新任务：仿真软件人员技能培训

- 议题

■ 服务器平台的使用（针对波动计算）

■ B8 SRW仿真（Oasys，Sirepo）

摘要

https://www.sirepo.com/light#/homehttps://www.aps.anl.gov/Science/Scientific-Software/OASYS

## B8布局


HEPS @ IHEP | 3


HEPS @ IHEP | 4

## SRW@OASYS

### 单电子发光

### 多电子追迹

光源 | 样品脚本
a) 计算速度快
b) 评估束线布局的正确性
a) 耗时长
b) 评估束线最终性能


HEPS @ IHEP | 5

SE-代码

ME-代码

### 并行运算

mpiexec –np 30 python ME_Script.py


HEPS @ IHEP | 6

## SRW@OASYS

晶体参数设置 | 反射镜设置

https://github.com/yangfg-bsrf/BEAMLINE-DEISIGN-HEPS/tree/master/Simulations/error_generation

HEPS @ IHEP | 7

## 误差问题是束线设计的重点，要求开展仿真设计

# 1. 合理的表征方式：例如聚焦性能


HEPS @ IHEP | 8

### 光斑尺寸 vs. 观察位置

### 光斑尺寸 vs. 观察位置

## Problem：存在误差时


HEPS @ IHEP | 9

XY或者ZY截面图

### 信息量更大

# 2. B8仿真计算设计与分析


HEPS @ IHEP | 10
| | | | 二次光源* 1μm (V) | 亚微米聚焦 nm | 微米聚焦 μm
单电子 发光 | 无误差 | 理论 | 几何 | 1.62 | 65 × 85
| | | 波动 | 1.33 | 62 × 123
| | 仿真 | 几何 | 1.62 | 60 × 80
| | | 波动 | 1.21 | 56 × 127
| 有误差 | 理论 | 几何 | 12.7 | 65 × 263
| | | 波动 | 12.7 | 65 × 260
| | 仿真 | 几何 | 15(范围) | 60 × 260
| | | 波动 | 15(范围) | 54 × 128
多电子 发光 | 无误差 | 理论 | 几何 | 2.17 | 201×113
| | | 波动 | 2.17 | 205× 152
| | 仿真 | 几何 | 2.18 | 170 ×100
| | | 波动 | 2.09 | 177 × 135
| 有误差 | 理论 | 几何 | 12.7 | 201 × 263
| | | 波动 | 12.7 | 205 × 263
| | 仿真 | 几何 | 20(范围) * 2 | 170 ×240
| | | 波动 | 20(范围) | 172×130
Note | *1：只列处垂直光斑尺寸 *2：未列出的地方，均指 FWHM

与设计结果的偏离，Why?

A. 仿真参数？
B. 误差的问题？
C. 软件的问题？
D. 设计上欠考虑？

HEPS @ IHEP | 11

# B8束线波动仿真 - 感悟

## 对于HEPS来说，仿真计算是一个实验研究工作，特点：

### 仿真工具本身及使用方法的正确性，需要验证

✓ 理论推导

### ✓ 不同软件复核

### ✓ 设计仿真实验

### 仿真实验的设计，能够说明设计的问题

### ✓ 束线牵涉的问题多方面，分离要素

- 出现问题，解决问题非常费劲。

### ✓ 计算量的优化，例如：

- 特别是波动计算，几何-波动配合使用；
- 画图尺寸、分辨率的搭配；


HEPS @ IHEP | 12

# 想法：仿真软件工作组

### 1. Github：代码分析

### 2. 提出、解答各类设计问题（借鉴）

A. 束线设计问题
B. 简单的各类软件设置方法（解决不了，再问作者）

### 3. 根据个人爱好，组建仿真工作组

分享：

- 已调试成功代码
- 设计文件
- 误差数据库

HEPS @ IHEP | 13

## 光学系统仿真工作规划（长期）：start-to-end simulation

新的四代同步辐射光源是未来发展的必然方向，可以支撑先进实验方法的高质量实施，进而 推动整个基础科学研究的发展。在此过程中，束线仿真平台是支撑先进光源束线的建设、发 展、运行重要支撑工具。

首先，服务于束线设计（设计端）；束线设计建设是一个工程性的工作，牵涉到性能、成本、 风险、周期等因素。在当前的技术水平下，随着各种误差问题复杂化，导致束线设计优化带 来困难。需要从底层研究分析具体的误差特征影响，避免束线设计参数的over - or under-specification。在现有条件下我们很难全面开展实验研究的情况下，数值仿真工具是最为有效 的研究手段。

其次，服务于束线设计（需求端）；光束线的终端应用-实验站样品测量是评价整个系统性 能最可靠、严谨的依据。由于工作性质、工程问题的差异，设计论证上往往是把两个环节作 为甲乙方分开，束线的仿真只能进行到样品处。为了最大利用四代光源产生的优质同步光， 落后的X射线光学技术要求光束线-实验站设计集成在一起，亟需通过仿真实验研究，优化实 验站的束线设计需求。

最后，服务于束线运行（仿真实验研究）；随着光线束线工程建设的完成，光束束线的高效 运行和发展成为重要任务。新实验技术方法的优化方向非常多，与样品、数据处理方法等密 切相关。为最大化利用束线产生的X射线，在开展在线研究之前，利用仿真平台开展针对性 的实验设计（包括束线参数）优化非常重要。

Draft by 贾全杰 & 杨福桂；Aim for the SR community

HEPS @ IHEP | 14

## 光学系统仿真工作规划（长期） ：start-to-end simulation

Draft by 贾全杰 & 杨福桂；Aim for the SR community

然而，考虑到衍射极限环光源与传统三代光源本身特征上的差异，效率高、精度高、功 能全等新需求对现有的束线仿真软件构成新的挑战。需要强调的是，衍射极限环的束线 设计专业化是必然趋势，也是任何一个光源的最优选择。从上面的分析来看，该工作要 求设计人员对实验方法、束线技术及软硬件都有很高了解，因此，培养高水平人才队伍 是一项长期的任务。需要建立国内光源束线设计人员的交流协作平台，营造束线设计职 业发展的大环境。最终共同解决新一代同步辐射光源面临的问题。

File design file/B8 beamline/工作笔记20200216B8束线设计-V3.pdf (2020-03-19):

# HEPS 工程工作笔记

## HEPS Technical Note

标题（Title） | B8 束线设计 – 第三版光学设计计算
作者 (Author)/ 系统 (System) | 杨福桂 | 日期 (Date) | 2020-2-16
编号 (Serial No.) | | 页数 (Pages) | 共 页 (含附件)

摘要 (abstract)：

根据 2.13-2.16 的讨论沟通，相比于 2019 年 2 月份的方案，B8 束线设计的调整思路：低能段

使用四镜谐波抑制镜，这样可以减少工程造价，提高高能段光束品质（此时无谐波镜）。微米

聚焦方案中，将 KB 镜后移，虽然影响了光通量，但是可以保证样品点的重合。在此思路下

开展以下评估：

（1）谐波抑制的计算，评估有无谐波镜，影响能段及效果；

（2）束线性能的计算，评估微米聚焦和亚微米聚焦两个模式的性能。

结论：

会 签 Concurred by

有效性 Validation | 填表人 Prepared by | 审 核 Reviewed by | 批 准 Approved by
签 名 Signature | XX
日期 Date | XX（一定写上日期）

### 1 束线光学设计综述

### 1.1 系统接收角

在讨论束线布局前，首先根据光源特征选定系统接收角。表格 1-1 给出了 10keV 下各接 收角度对应的通量。可见，束线接收角为 18μrad×18μrad 接收的通量占总通量的 90%， 且角度变大增益变小。因此单色光的最大接收角设置为 18μrad×18μrad。

表格 1-1 插入件不同 K 值下各接收角对应的光通量

接收角度 µrad×µrad | 接收光通量 ph/s/0.1%BW @ 10keV
30×30 | 7.5e14
25×25 | 7.4e14
20×20 | 7.0e14
18×18 | 6.8e14
16×16 | 6.2e14
14×14 | 5.4e14

对于白光镜，考虑到边缘效应，系统的接收角为 25μrad×25μrad。在此基础上，我们确定 各反射镜的长度。

### 1.2 反射镜反射率

为了满足束线能区范围 4.8keV - 45keV 及能扫的要求，且保证能量变化时，反射镜（不 包括谐波抑制镜）的掠入射角不变。从图可以看到，Pt@1.7mrad 和 Si@1.7mrad 的组合 是合适的，即反射镜以 Si 为基底，部分镀 Pt，以 1.7mrad 入射。


图 1-1 Si、Pt、Rh 反射率曲线

在能量低于 17keV 时，使用 Si 作为反射面；能量在 17-45keV 时，使用 Pt 作为反射面。 据此反射率曲线 Si@1.7mrad，可以看到 7keV 以下的能量段存在谐波问题。为此，可通 过单色器失谐或者添加谐波抑制镜解决。在使用大光斑进行实验时，可以使用失谐；谐 波抑制镜位于紧贴 SSA，减少面型误差对二次光源光斑尺寸的影响。为了确定谐波镜镀 层，图 1-2 给出了 Si、Rh、Ni 和 Pt 在不同掠入射角下的反射率曲线。可以看到 Pt@8mrad 或者 Rh@7mrad 即可保证反射率，又可保证 4.8-7keV 的谐波抑制比。


图 1-2 不同材料镀层的反射率

### 1.3 束线设计考虑

### 1.3.1 束线设计的整体考虑

表格 1-2 B8 束线光学设计考虑因素

输入因素 | 问题点 | 设计方案对策 | 输出

能量范围 4.8keV - 45keV | 高能反射 | 系统掠入射角 | Pt，1.7mrad
| 低能反射 | 镀层类型 | Si、Pt
| ？
能量扫描 (至 1keV) | 能扫出高变化 | 单色器前准直 | 准直反射镜
| 变能量点 CCM 出 高变化 | Channel-cut 晶体设计 | 分段式 CC
| | 谐波镜的补偿 | 四镜、双镜方案
| 能扫热变形 | 布局 | 亚微米次级聚焦方案
谐波抑制比 0.001 | 低能谐波比不足 | 微米快扫下谐波抑制反射镜 | 四镜、双镜方案
| | 亚微米模式下单色器失谐 | DCM 方案
聚焦性能 尺寸：300nm 距离：150mm | 微米聚焦与亚微 米聚焦的配合 | 亚微米：DCM VFM、sub-micron-KB 微米：VCM、CCM、VFM、HRMs、 micron-KB | 器件数量与类型
| | 聚焦方案 | 次级聚焦方案
造价
工程风险
使用性能

### 1.3.2 聚焦性能优化考虑

利用相空间理论研究束线布局的优化。这里主要考虑反射镜的接收口径及工作距离因素。 很容易得到样品处的相空间尺寸为：

PSH,V

′ =

lH,Vθ

qH,V

sH,V

′

其中，lH是发射镜的长度，θ是反射镜掠入射角，qH,V是像距，sH,V

′ 是成像聚焦光斑尺寸。


图 1-3 光学传输系统的一般模型

首先考虑最大接收效率的问题，如果整个光学传输系统没有误差，则整个系统的传

输过程中，相空间尺寸守恒，根据 IHEP-HEPS-OS-EN-2020-001 文档中关于相空间计算 的方法，可以获得系统最大传输效率：

EF =

PSH,V

′

PSH,V

=

PSH,V

′

αH,VsH,V

其中，qH = lH/2 + W，W 是工作距离。

当光学传输系统的器件存在误差时，为了减小分析的复杂度，可以等效到虚拟光源尺寸。 例如，反射镜的位置为 37m，面形误差为 0.3 μrad，则光源的展宽为 2*2.35*37*0.3 = 52 μm。

（1）对于 B8 束线来说，亚微米聚焦下，假设反射镜长度最大为 300mm，样品点尺 寸 0.30 μm × 0.30 μm，工作距离 150mm，由此可以计算垂直和水平总的相空间尺寸
为 | ： | 1.7mrad*300mm*1.7mrad*300mm*0.30μm*0.30μm/(300mm*600mm)
=0.13μm²

·mrad²，样品处的光斑尺寸为 44 μm × 18μm，如果接收角 18 μrad × 18μrad， 对应的相空间尺寸为 0.25μm²

·mrad²，也就是说最大效率为 0.52，当按照 200nm 光 斑设计是，效率为 0.23。也就是说，聚焦光斑尺寸的设计值，极大决定了系统效率。

（2）对于 B8 束线来说，微米聚焦模式下，与其他束线一样，面形误差是系统性能 的重要贡献者，扩展了系统的相空间尺寸。当反射镜的长度为 600mm，掠入射角
1.7mrad | ， | 工 | 作 | 距 | 离 | 为 | 1.5m | ， | 样 | 品 | 点 | 的
1.7mrad*0.6m*1.7mrad*0.6m*2μm*2μm/(1.5m*1.8m) =1.54μm²

·mrad²，远大于光源的
相空间尺寸，说明微米聚焦模式的效率是没有问题的。

（3）综合以上两点来看，微米聚焦和亚微米聚焦两个模式，为了优化通量，亚微米 聚焦应优先考虑。需要注意这里仅仅考虑了聚焦成像效果，从器件类型及大致布局 又受限于快扫微米聚焦模式。

另外一方面，根据以上，虚拟光源的尺寸sH,V确定的情况下，也可以确定光源处的最大

接收角度：

αH,V =

lH,Vθ

qH,V

sH,V

′

sH,V

=

lH,Vθ

MH,VqH,V

MH,V是整个系统的缩放比。例如，对于亚微米聚焦，如果考虑仅有两个垂直反射镜的相

空间扩展至 52 μm*1.414 = 73μm，那么，系统最大接收角为 0.13/73/42 = 42μrad²。目前 亚微米聚焦模式采用 8.3μrad*5.6μrad = 46μrad²。即当前的设计，相空间已达到理论极限。

### 1.4 束线布局配置

束线布局如图 1-4 所示，水平方向采用直接聚焦方式，垂直方向采用二级聚焦方式。


首先，确定系统的接收角度，亚微米模式的接收角为 0.3*1.7/61 = 8.3μrad（水平）， 0.3*1.7/11*4.5/37 = 5.6μrad（垂直）。如表格 1-1 所示，18 μrad × 18 μrad 基本接收了大部 分的通量，考虑到相空间的尺寸不是问题，因此设定微米聚焦模式的接收角为 18 μrad ×18 μrad。

图 1-4 仿真布局图

### 2 亚微米聚焦方案性能

对于亚微米聚焦，水平方向采用直接聚焦的方案，这样主要由缩放比来决定水平聚 焦的光学布局。根据光源尺寸 42um，保证一定冗余下，设计样品点尺寸为 200nm，由 此可以计算水平缩放比 M 要达到 210（。

图 2-1 反射镜面形误差 VCM 和 VDM 反射镜的面形误差曲线，在全口径内的斜率误 差为 0.3 μrad rms

追迹亚微米模式，次级光源点处的光斑分布。


图 2-2 无误差时的二次光源处的追迹结果

加载面形误差后，在 49.5m 处和偏离 49.9m 处的光斑尺寸，即离焦 0.4m。在实际操作 中，该误差通过调节VCM的压弯量补偿，为了简化问题，这里调节 VFM的焦距至4.2m， 将最小光斑焦点移动到 49.5m 附近，见图(d)。但是我们要认识到在能扫过程中面形误差 的会发生变化，进而导致这种最佳焦点位置的移动，因此应避免这类问题。


图 2-3 VFM 和 VCM 加载面形误差后的追迹结果，二次光源处。(a) 0mm, (b) 300mm,
(c) 聚焦变化曲线


图 2-4 VFM 焦距调整后的追迹结果，二次光源处。(a) -300mm, (b) 0mm, (c) 聚焦变 化曲线

亚微米聚焦光斑的情况，下图分别给出了，光源尺寸、发散角、VCM-footprint，单色器 出光（d）、VFM-footprint（e）、二次光源分布、VKB-footprint（g）和 HKB-footprint（h） 以及样品处的光斑（i）。

(a) (b)


(c) (d)
(e) (f)
(g) (h)


(i)
图 2-5 亚微米聚焦情况，各器件上的光场分布

谐波情况的计算情况如下，表中给出了各个器件后的通量追迹结果。同时，R_ratio_mirr 是理论计算的反射镜反射率的谐波比，它是决定器件谐波抑制贡献能力的体现，与追迹 结果一致。阴影部分是起到谐波抑制的主要部件。可见单色器和反射镜共同构成了谐波 抑制的主体。当能量小于 6keV 时，只有单色器和光源对谐波有抑制作用，满足不了谐 波抑制的要求。当能量点在 7keV 时，反射镜 VCM 和 VFM 共同贡献下逐渐满足谐波要 求。7.5keV 已能够满足谐波抑制的需求。
| 光源 | VCM | DCM | VFM | VKB | HKB
5@1st | 3.13e14 | 3.03e14 | 2.8e13 | 2.7e13 | 1.50e13 | 1.40e13
3rd | 1.3e14 | 1.28e14 | 1.08e12 | 1.06e12 | 5.72e11 | 5.49e11
谐波比 | 0.415 | 0.42 | 0.038 | 0.039 | 0.038 | 0.039
R_ratio_mirr | | 1.01 | 0.090 | 1.01 | 1.02 | 1.02
6@1st | 3.12e14 | 3.03e14 | 3.13e13 | 3.05e13 | 1.66e13 | 1.53e13
3rd | 8.61e13 | 8.17e13 | 7.33e11 | 6.96e11 | 3.67e11 | 3.47e11
谐波比 | 0.28 | 0.27 | 0.023 | 0.023 | 0.021 | 0.023
R_ratio_mirr | | 0.97 | 0.078 | 0.97 | 1.02 | 1.02
7@3st | 1.49e14 | 1.45e14 | 1.62e13 | 1.58e13 | 8.75e12 | 8.06e12
9th | 5.42e13 | 6.38e12 | 5.55e10 | 6.54e9 | 3.73e9 | 3.39e9
谐波比 | 0.36 | 0.044 | 3.43E-03 | 4.14E-04 | 4.26E-04 | 4.21E-04
R_ratio_mirr | | 0.12 | 0.078 | 0.12 | 1.01 | 1.01
7.5@3rd | 1.54e14 | 1.51e14 | 1.76e13 | 1.72e13 | 9.42e12 | 8.66e12
9th | 5.10e13 | 3.58e12 | 3.52e10 | 2.48e9 | 1.49e9 | 1.38e9
谐波比 | 0.33 | 0.024 | 0.002 | 1.44e-4 | 1.58e-4 | 1.59e-4
R_ratio_mirr | | 0.07 | 0.083 | 0.07 | 1.01 | 1.01

为了更直观体现谐波贡献，这里计算


假设光源和单色器在 6-8keV 处不存在谐波抑制的跳变，设光源的谐波比为 0.42，单色 器的谐波比为 0.09，为了达到 1e-3 的谐波抑制，要求反射镜的谐波抑制为 0.034。 当亚微米聚焦模式选择 VFM 和 VCM 是 Si - 1.7mrad，KB 是 Rh-2mrad 镀层，那么只能 要求 VFM 和 VCM 的谐波抑制比例为 0.16，对应的能量点底线为 6.7keV。当能量小于 6.7keV 时，需要考虑其他谐波抑制方案。
当亚微米聚焦模式选择 VFM、VCM 和 KB 均为 Si - 1.7mrad，对应的谐波抑制比为 0.4， 对应的能量点为 6.3keV。 这种情况对应的微米聚焦的情形。

### 3 微米聚焦方案性能

### 3.1 反射镜误差对聚焦的影响


在亚微米聚焦中，光斑只是用了反射镜 VCM、VFM 的一个部分，而反射镜的误差选择 是按照全局设计的。下图给出了 0 点位置和偏移 50mm 位置的光斑形状。以及焦点变 化，此时 VFM 的焦距已调整为 4.5m。


### 3.2 谐波情况

| 亚微米 | 微米聚焦
| 光源 | 单色器 | 光源 | 单色器
7.5 | 1.55E+14 | 1.78E+13 | 7.55E+14 | 8.66E+13
| 5.11E+13 | 4.98E+11 | 2.05E+14 | 1.78E+12
| 3.30E-01 | 2.80E-02 | 2.72E-01 | 2.05E-02
| | 8.48E-02 | | 7.55E-02
7 | 1.49E+14 | 1.69E+13 | 7.58E+14 | 8.39E+13
| 5.45E+13 | 4.37E+11 | 2.17E+14 | 1.86E+12
| 3.65E-01 | 2.59E-02 | 2.87E-01 | 2.22E-02
| | 7.09E-02 | | 7.73E-02
6.8 | 1.48E+14 | 1.65E+13 | 7.58E+14 | 8.39E+13
| 5.49E+13 | 5.19E+11 | 2.26E+14 | 2.05E+12
| 3.71E-01 | 3.14E-02 | 2.98E-01 | 2.45E-02
| | 8.47E-02 | | 8.21E-02
6.6 | 2.96E+14 | 3.20E+13 | 9.79E+14 | 1.06E+14
| 6.01E+13 | 5.39E+11 | 1.56E+14 | 1.49E+12
| 2.03E-01 | 1.69E-02 | 1.59E-01 | 1.41E-02
| | 8.32E-02 | | 8.84E-02
6.4 | 3.03E+14 | 3.24E+13 | 1.02E+15 | 1.11E+14
| 6.83E+13 | 6.56E+11 | 1.82E+14 | 1.57E+12
| 2.26E-01 | 2.02E-02 | 1.78E-01 | 1.42E-02
| | 8.96E-02 | | 7.96E-02
6.2 | 3.08E+14 | 3.23E+13 | 1.06E+15 | 1.11E+14
| 7.73E+13 | 7.24E+11 | 2.05E+14 | 2.05E+12
| 2.51E-01 | 2.24E-02 | 1.93E-01 | 1.86E-02
| | 8.95E-02 | | 9.60E-02

6 | 3.12E+14 | 3.27E+13 | 1.11E+15 | 1.17E+14
| 8.57E+13 | 8.47E+11 | 2.39E+14 | 2.28E+12
| 2.75E-01 | 2.59E-02 | 2.15E-01 | 1.94E-02
| | 9.41E-02 | | 9.02E-02
首先计算光源一定口径接收角下，插入件谐波比的情况。


接着光线追迹光源-单色器的谐波抑制效率。

| 亚微米 | 微米聚焦
能量 keV | 光源 | 单色器 | 光源 | 单色器
7.5@3 | 1.55E+14 | 1.78E+13 | 7.55E+14 | 8.66E+13
| 5.11E+13 | 4.98E+11 | 2.05E+14 | 1.78E+12
| 3.30E-01 | 2.80E-02 | 2.72E-01 | 2.05E-02
| | 8.48E-02 | | 7.55E-02
7@3 | 1.49E+14 | 1.69E+13 | 7.58E+14 | 8.39E+13
| 5.45E+13 | 4.37E+11 | 2.17E+14 | 1.86E+12
| 3.65E-01 | 2.59E-02 | 2.87E-01 | 2.22E-02
| | 7.09E-02 | | 7.73E-02
6.8@3 | 1.48E+14 | 1.65E+13 | 7.58E+14 | 8.39E+13
| 5.49E+13 | 5.19E+11 | 2.26E+14 | 2.05E+12
| 3.71E-01 | 3.14E-02 | 2.98E-01 | 2.45E-02
| | 8.47E-02 | | 8.21E-02
6.6@1 | 2.96E+14 | 3.20E+13 | 9.79E+14 | 1.06E+14
| 6.01E+13 | 5.39E+11 | 1.56E+14 | 1.49E+12
| 2.03E-01 | 1.69E-02 | 1.59E-01 | 1.41E-02
| | 8.32E-02 | | 8.84E-02
6.4@1 | 3.03E+14 | 3.24E+13 | 1.02E+15 | 1.11E+14
| 6.83E+13 | 6.56E+11 | 1.82E+14 | 1.57E+12
| 2.26E-01 | 2.02E-02 | 1.78E-01 | 1.42E-02
| | 8.96E-02 | | 7.96E-02
6.2@1 | 3.08E+14 | 3.23E+13 | 1.06E+15 | 1.11E+14
| 7.73E+13 | 7.24E+11 | 2.05E+14 | 2.05E+12

| 2.51E-01 | 2.24E-02 | 1.93E-01 | 1.86E-02
| | 8.95E-02 | | 9.60E-02
6@1 | 3.12E+14 | 3.27E+13 | 1.11E+15 | 1.17E+14
| 8.57E+13 | 8.47E+11 | 2.39E+14 | 2.28E+12
| 2.75E-01 | 2.59E-02 | 2.15E-01 | 1.94E-02
| | 9.41E-02 | | 9.02E-02

从表中可以看出这两个设备的谐波比总贡献基本上在 0.02 的水平。单色器的谐波抑制 性能基本在 10%-7%的水平。大接收口径和小接收口径中，单色器和单色器的比重各有 不同。

### 3.3 聚焦光斑性能

单色器后和二次光源处的光斑分布，通量分别为 7.76e13 和 7.61e13phs/s。


KB 镜加载误差如下图所示。


有无误差时，聚焦光斑的分布：


改变观察平面位置，我们看到 0 平面基本上时最小光斑位置，即焦点位置。


### 4 聚焦位置的确定

### 5 存在问题

反射镜的面形误差局域与全局的不同，给仿真带来了不确定性。本仿真过程中，将居于 面形误差补偿至最佳，但是对于能量扫描应用，出高问题有可能会带来不确定的结果。

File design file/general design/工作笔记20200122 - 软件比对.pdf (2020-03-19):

# HEPS 工程工作笔记

## HEPS Technical Note

标题（Title） | SRW 和 XRT 的波动计算复核 1 – 光源发光特征的计算
作者 (Author)/ 系统 (System) | 杨福桂 | 日期 (Date) | 2020-2-7
编号 (Serial No.) | | 页数 (Pages) | 共 页 (含附件)

摘要 (abstract)：

以 HEPS-B3 和 B8 两条束线为模型，使用 XRT 和 SRW 计算光源发光和电子束团发光特

性。主要考虑单电子与多电子发光特性，以及仿真软件波动计算结果的比对。

会 签 Concurred by

有效性 Validation | 填表人 Prepared by | 审 核 Reviewed by | 批 准 Approved by
签 名 Signature | XX
日期 Date | XX（一定写上日期）

### 1 束线光学设计需求综述

HEPS-B3 和 B8 分别处于低和高 beta 直线节。储存环和光源参数如表格 1 1 所示。

HEPS-B3 | HEPS-B8
储存环
电子能量 (GeV) | 6 | 6
电流强度 (GeV) | 0.2 | 0.2
能散 | 0.00111 | 0.00111
电子尺寸 (μm) | 8.8*2.3 | 16.7*5.1
电子束团发散角 (μrad) | 3.1*1.2 | 1.65*0.53
Beta function | 2.84*1.92 | 10.12*9.64
发射度 (pm*rad) | 27.28*2.76 | 27.55*2.70
插入件
能量点@谐波级次 | 23keV@1st | 10keV@3st
λ/2π (pm.rad) | 19.74 | 19.74
周期 (mm) | 12 | 35
周期数 | 180 | 142
表格 1-1 光源参数列表

### 2 仿真束线布局

由于光源处发光点的位置非确定，因此这里需要从波动计算结果分析光源尺寸。仿真束 线布局图如图 2-1 所示。这里使用了椭圆柱面形的 KB 镜作为聚焦器件。为了去除口径 衍射的影响， KB 镜的接收角度大于 4σ，这里选择为 25μrad。考虑掠入射角 4mrad，对 应的反射镜长度约为 250mm。基于此，确定反射镜位置为 40m 和 40.3m，反射镜长度为 300mm。


图 2-1 仿真布局图

### 3 SRW 波动仿真计算

### 3.1 单电子发光波动计算

光源出射到 40m 位置时的光场分布，半高全宽为 304μm×312μm，传播距离为 40m，由 此可以计算光束发散角为 7.6μrad×7.8μrad FWHM，或者 3.23μrad×3.32μrad RMS。


图 3-1 40m 处光场分布

为了观察光源的光斑尺寸，SRW 提供了两种方法，如图 3-2 所示。一种是通过 Back Propagation 组件，把波前逆向传播至光源处；第二种方式是使用理想透镜成像，缩放比 为 1:1。为了与 XRT 计算对应，这里同时考虑第三种方式，即 KB 镜聚焦，该模式下缩 放比分别为 1.01:1(H)和 1:1(V)。结果如图 3-3 所示，光源点的单光子发光尺寸为 12.5 μm×12.5 μm FWHM，5.37μm×5.37 μm RMS。注意这里的统计值直接由 FWHM 算出， 因此与图中显示值有所差异。


图 3-2 SRW 光源尺寸测量


(a)


(b)


(c)
图 3-3 SRW 三种不同方式计算的单光子发光尺寸

### 3.2 电子束团波动计算

接着考虑电子束团，SRW 提供两种考虑电子束团尺寸的方案，一种是 Monte Carlo 追迹，另外一种是卷积，该计算由单电子追迹卷积直接获得。对应图 3-3，图 3-4 给出

了卷积的计算结果。


(a)


(b)
图 3-4 理想透镜成像和 KB 镜成像的多电子卷积结果

接着开展对 SRW 多电子束团的 Monte-Carlo 计算，分别对应理想透镜和 KB 镜成像 两种方式。如图 3-5 所示，追迹电子数为 10000，光斑的半高全款分别为 41.96 μm×17.07 μm 和 41.14μm×17.20 μm，二者结果接近。


(a)


(b)
图 3-5 理想透镜(a)和 KB 镜(b)成像样品处的光斑分布

### 4 XRT 波动仿真计算

### 4.1 单电子发光波动计算

在 XRT 中将系统的发射度和能散设置为 0，可以模拟单电子发光的情况。图 4-1 给出了 典型位置的追迹结果。从图(b)可以得到单电子发光的角度为 312/40=7.8μrad，从图(b)可 以得到发光尺寸为 5.86μm *2*40.3m/39.7m=11.89μm(H)，6.33μm *2=12.66μm(V)。


(a)


(b) (c)
图 4-1 光源发散角(a)，VKB 位置(b)和样品处(c)的光场分布

### 4.2 电子束团波动计算

追迹投点 10000 个，每个点计算 5e4 个光线，计算单个能量点的情况。仿真结果如图 4-2 所示，图(a)显示电子投点数已经能够体现电子束团的特征。图(b)和图(c)显示光场的发散 角为 6.43*2 = 12.86μrad(H)，6.85*2=13.7μrad(V)。图(d)给出了样品处光斑尺寸为 21.48*2*40.3/39.7 = 43.6μm(H)，8.67*2*40/40 = 17.34μm(V)。

(a) (b)
(c) (d)

图 4-2 XRT 电子束团追迹图，分别是电子束团分布(a)，发散角，VKB 位置和样品处 光场分布

### 5 总结

同样开展 B3 束线的仿真，B3 和 B8 束线的统计结果如表 5-1 所示。SRW 多电子波前的 发散角比 XRT 稍微大一些，差异再 10%以内。这里数值的差异还需要考虑计算精度、 显示图像的精度等因素。

| HEPS-B3 | HEPS-B8
FWHM | XRT | SRW | XRT | SRW
单电子发光尺寸 (μm) | 5.32×5.32 | 5.53×5.53 | 11.89×12.66 | 12.5×12.5
单 电 子 发 光 发 散 角 (μrad) | 7.88×7.88 | 7.72×7.72 | 7.8×7.8 | 7.6×7.8
总发光尺寸 (μm) | 21.1×7.4 | 22.25×8.0 | 43.6×17.34 | 41.14×17.20
总发散角(μrad) | 10.42×9.76 | 11.47×9.7 | 12.86×13.7 | 12.9×13.87
表 5-1 光源特性计算值汇总

作为参考，根据理论计算，可以得到 B8 束线的结果：
Single electron radiation size = (x)5.587 µm RMS，13.1µm FWHM
Single electron radiation divergence = (x)3.532 µrad RMS，8.3µrad FWHM
Single electron radiation emittance = 19.733 pm rad
Total photon size (x)17.710 and (y)7.801 µm RMS，(x)41.6 and (y)18.33 µm FWHM Total photon divergence (x)6.073 and (y)5.868 µrad RMS，(x)14.27 and (y)13.789 µrad FWHM

B3 束线的结果：
Single electron radiation size = (x)2.429 µm RMS，5.71 µm FWHM
Single electron radiation divergence = (x)3.532 µrad RMS，8.30µrad FWHM
Single electron radiation emittance = 8.579 pm rad
Total photon size (x)9.136 and (y)3.364 µm, (x)21.470µm and (y)7.906 µm FWHM
Total photon divergence (x)5.281 and (y)4.441 µrad，FWHM (x)12.411 and (y)10.436 µrad

为了方便观察曲线的差异，将中心线的分布画在同一幅图里，如图 5-1 和图 5-2 所 示。单电子情况下，只考虑 40m 处的光场分布，和样品处的光场分布。SRW 和 XRT 均 使用 KB 聚焦模式计算情况。单电子成像完全一致。但对于电子束团的曲线，投点数 1e4 仍有待进一步提高。但垂直方向的一致性，说明该计算结果的正确性。


(a)


(b)
图 5-1 单电子追迹结果，VKB(a)和样品(b)处的光场分布


(a)


(b)
图 5-2 多电子追迹结果，VKB(a)和样品(b)处的光场分布

### 6 工作中的问题

（1）XRT 的 KB 镜建模过程中发现，KB 镜聚焦参数设置仍需进一步考虑，按照现在的 参考，VKB 和 HKB 焦点不重合，且中心位置偏离预期中心，当掠入射角减小为 2e-3rad 时，该值减小到很小。但该误差不影响本算例的计算结论。

（2）KB 聚焦计算中，SRW 的图像中心位置偏离波动计算光斑中心位置，这包括 VKB 的位置和样品位置。多电子追迹存在此问题，单电子追迹未发现该问题。

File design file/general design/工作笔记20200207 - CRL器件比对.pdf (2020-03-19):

# HEPS 工程工作笔记

## HEPS Technical Note

标题（Title） | CRL 器件 – XRT 和 SRW 波动计算比对
作者 (Author)/ 系统 (System) | 杨福桂 | 日期 (Date) | 2020-2-7
编号 (Serial No.) | | 页数 (Pages) | 共 页 (含附件)

摘要 (abstract)：

复合折射率透镜（CRL）是高能同步辐射光源 HEPS 的重要器件。为了保证仿真计算的 正确性，需要对不同软件下 CRL 聚焦性能的评估。这里考虑 B3 和 B8 两条束线，在单色光 情况下的聚焦情况。
需要考虑口径、焦距（组数）等因素的影响。

会 签 Concurred by

有效性 Validation | 填表人 Prepared by | 审 核 Reviewed by | 批 准 Approved by
签 名 Signature | XX
日期 Date | XX（一定写上日期）

### 1 束线光学设计综述

HEPS-B3 和 B8 分别处于低和高 beta 直线节。储存环和光源参数如表格 1 1 所示。

HEPS-B3 | HEPS-B8

储存环

电子能量 (GeV) | 6 | 6
电流强度 (GeV) | 0.2 | 0.2
能散 | 0.00111 | 0.00111
电子尺寸 (μm) | 8.8*2.3 | 16.7*5.1
电子束团发散角 (μrad) | 3.1*1.2 | 1.65*0.53
Beta function | 2.84*1.92 | 10.12*9.64
发射度 (pm*rad) | 27.28*2.76 | 27.55*2.70

插入件

能量点@谐波级次 | 23keV@1st | 10keV@3st
λ/2π (pm.rad) | 19.74 | 19.74
周期 (mm) | 12 | 35
周期数 | 180 | 142

表格 1-1 光源参数列表

### 2 仿真束线布局

由于光源处发光点的位置非确定，因此这里需要从波动计算结果分析光源尺寸。仿真束 线布局图如图 2-1 所示。


图 2-1 仿真布局图

在 XRT、SRW 使用的折射率参数不同，δ = 1 − nreal。

| Attenuation length (m) | δ
| XRT | SRW | XRT | SRW
10keV | 0.0088357 | 0.0083543 | 3.40239e-06 | 3.413595e-06
23keV | 0.0270313 | 0.0265456 | 6.427981e-07 | 6.43869e-07

图 2-2 Be 透镜参数，考虑不同的软件

透镜焦距为f =

2R
δ

，基于 XRT 的折射率数据计算的透镜光焦度如表格 2-1。折射率差异 0.32%@10keV, 0.16%@23keV。考虑到系统的接收口径，B8 束线使用两个 300μm 曲率 半径的 Be CRL 组，焦距为 22.045m。在口径上，CRL 前放置了一个 1mm 直径的光阑， 对应的系统接受角约为 4σ。

R(μm) | φ (m⁻¹ )@10keV | φ (m⁻¹ )@23keV | D(mm)
50 | 0.13610 | 0.02571 | 0.504
100 | 0.0 | 0.0 | 0.716
200 | 0.0 | 0.0 | 1.008
300 | 0.02268 | 0.004285 | 1.236
500 | 0.0 | 0.0 | 1.588
1000 | 0.0 | 0.0 | 2.256
2000 | 0.0 | 0.0 | 3.188
表格 2-1 CRL 特性参数表

由于本工作的主要目的是 XRT 软件和 SRW 软件中 CRL 组件计算结果的比对。这里主 要考虑单电子发光。

### 3 SRW 波动仿真计算

为了观察光源的光斑尺寸，SRW 提供了两种方法，如图 3-1 所示。一种是通过 Back Propagation 组件，把波前逆向传播至光源处；第二种方式是使用理想透镜成像，缩放比 为 1:1。第三种方式是使用真实的 CRL。 由于长焦距和短焦距 CRL 的性能有所差异， 包括吸收和光程差的变化，这里我们还要评估不同焦距透镜组的聚焦情况。在每一种计 算中，需要精确计算透镜焦距和像点位置。


图 3-1 SRW 仿真程序

### 3.1 长焦距情况（22m）

第三种方式是使用真实的 CRL，两个曲率半径为 300μm 的 Be 透镜。样品点位置在 88.18m 处，构成 1：1 成像。仿真结果如图 3-2 所示，光源点的单光子发光尺寸为 12.5 μm×12.5 μm FWHM，12.23μm×12.49 μm FWHM 和 12.36μm×12.36 μm。结果一致说明， 此时 CRL 接近理想成像。


(a)


(b)


(c)
图 3-2 SRW 三种不同方式计算的单光子发光尺寸，(a)backpropagation；(b)理想 CRL 和(c)真实 CRL 成像


(a)


(b)
图 3-3 理想透镜和真实 CRL 的 xy 截面图

### 3.2 短焦距情况（1m）

考虑使用 40 组 300μm 的 Be 透镜，可以计算焦距为 1.103m，像距为 1.131m。理想透镜 的焦距设置成 1.103m，对应像距为 1.131m。SRW 中真实透镜的焦距为 1.1002638279413， 对应的像距为 1.128m。考虑到像平面位置可能存在移动，这里计算了不同位置的光斑尺 寸，如表格 3-1 所示，可以看到 1.130m 处的光斑符合缩放比的，且处于局部最小。注 意，在计算中，推荐使用 Quadratic Term Special，该方法可以在比较小的采样数下获得 正确结果。图 3-5 更直观地给出了焦点位置的变化（纠错，SRW 结果的纵坐标需要减 小 10 倍）。红线理想成像位置点。

位置 | 理想透镜成像 | 真实 CRL
1.135 | 1.2289*1.2672 | 1.5837*1.6292
1.133 | 0.5107*0.5219 | 1.0619*1.0857
1.131 | 0.3254*0.3298 | 0.5191*0.5236
1.130 | 0.3152*0.3152 | 0.3046*0.3001
1.129 | 0.2372*0.2349 | 0.3093*0.3093
1.128 | 0.6360*0.6427 | 0.3082*0.3082
1.127 | 0.9945*1.0162 | 0.2951*0.2906
1.126 | 1.3243*1.3639 | 0.5235*0.5325
1.125 | 1.5995*1.6525 | 0.8031*0.8150
表格 3-1 不同位置处的光斑尺寸变化

1.130m 处的追迹结果见图 3-4，相比于理想透镜成像，很明显大角度位置的光场匀滑。



(d)
图 3-4 理想透镜聚焦(a)和真实 CRL 聚焦(b)的分布图，(c)一维曲线对比；(d)是理想透 镜成像 1.129m 处的分布


(a)


(b)
图 3-5 理想透镜聚焦(a)和真实 CRL 聚焦(b)的分布图 xy 截面图，y 为光线传播方向

### 4 XRT 波动仿真计算

### 4.1 长焦距情况（22m）

在 XRT 中将系统的发射度和能散设置为 0，可以模拟单电子发光的情况。图 4-1 给出了 典型位置的追迹结果。可以看出在透镜的焦点位置，光斑并不是最小位置。对比图 b 和 图 c，可以看出离焦位置峰值强度增加，但是分布偏离高斯分布，拖尾问题增加。


(a) (b)


(c) (d)
图 4-1 长焦距透镜的单电子波动传播结果

### 4.1 短焦距情况（1m）

在 XRT 中，透镜的模型是具有一定厚度和间距的薄板，因此透镜成像位置并不是从最 后一片透镜算起，需要寻找焦平面位置。在 XRT 中，可以使用光线几何追迹计算焦点 位置，图 4-2 给出了光斑尺寸在不同位置处的分布曲线(a)，样品处的光场分布(b)以及 xy 截面的分布(c)。偏置 80mm，总 CRL 长度为 120mm。由于光线追迹数的限制，xy 截


面图存在一定的毛刺，但这不影响焦点位置的判断。

(a) (b)

(c)
图 4-2 短焦距透镜的 XRT 几何追迹

接下来，开展单电子波动追迹，结果如图 4-3 所示。

(a) (b)


(c)
图 4-3 短焦距透镜的单电子波动传播结果

5 50 微米 CRL 聚焦仿真

改变透镜曲率半径，观察聚焦情况。这里考虑到透镜口径为 0.5mm，所以 SRW 和 XRT 中均对口径光阑限制为 0.5mm 圆形。SRW 中的 15 组透镜焦距 0.489 m，对应的像距为 0.4945m。

(a) (b)


(c) (d)

### 6 总结

为了方便观察曲线的差异，将中心线的分布画在同一幅图里，如错误!未找到引用源。所 示。很明显，对于长焦距，SRW 和 XRT 能获得完全一致的结果，包括 xy 截面分布也是 一致的。而对于短焦距透镜，三者存在差异，与理想透镜的差异，可以认为是光学透镜 的哑铃作用。


(a) (b)
图 6-1 XRT、SRW 波动计算一维曲线对比，(a)长焦距，(b)短焦距，其中图(b)中 SRW-理想透镜和真实透镜的焦点位置分别位于 1.130m，1.1285m，

修改透镜数为 80 片，焦距为 0.505m，从计算结果来看 SRW 和 XRT 计算结果一致，说 明二者的仿真方法是一致的，存在的微小差别应该来自于材料参数不完全一致。SRW 中 理想透镜和真实透镜的成像位置与理论计算值一致，这比 XRT 要方便很多。


(a) (b)


(c) (d)
图 6-2 XRT、SRW 波动计算结果，f=550mm，分别对应 XRT、SRW 理想透镜、 SRW 真实 CRL，以及三个一维曲线(d)

### 7 工作中的问题

（1）CRL 的有限厚度给焦点位置的确定带来了困难。

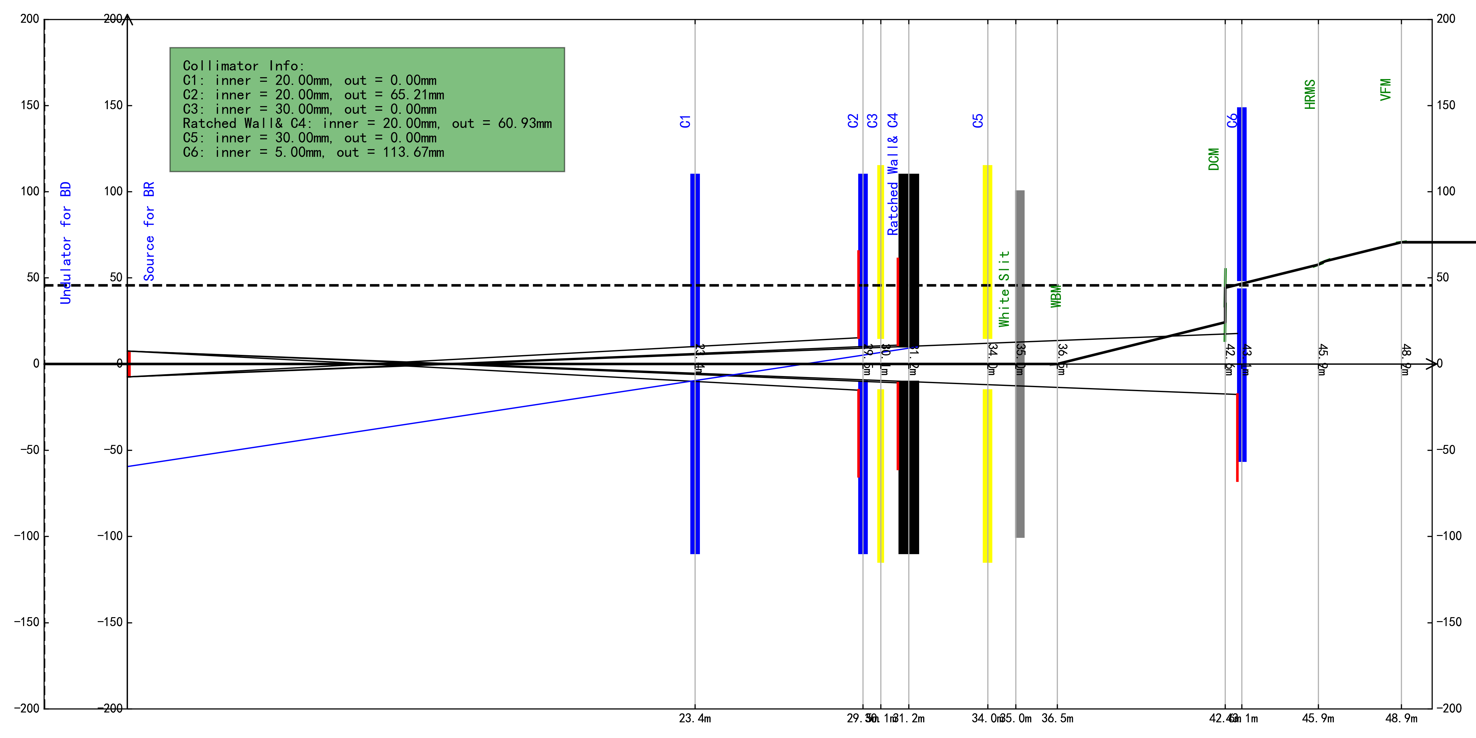
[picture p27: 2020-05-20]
Simulations/Radiation Shielding Design/tracing/Radiation_protection.png

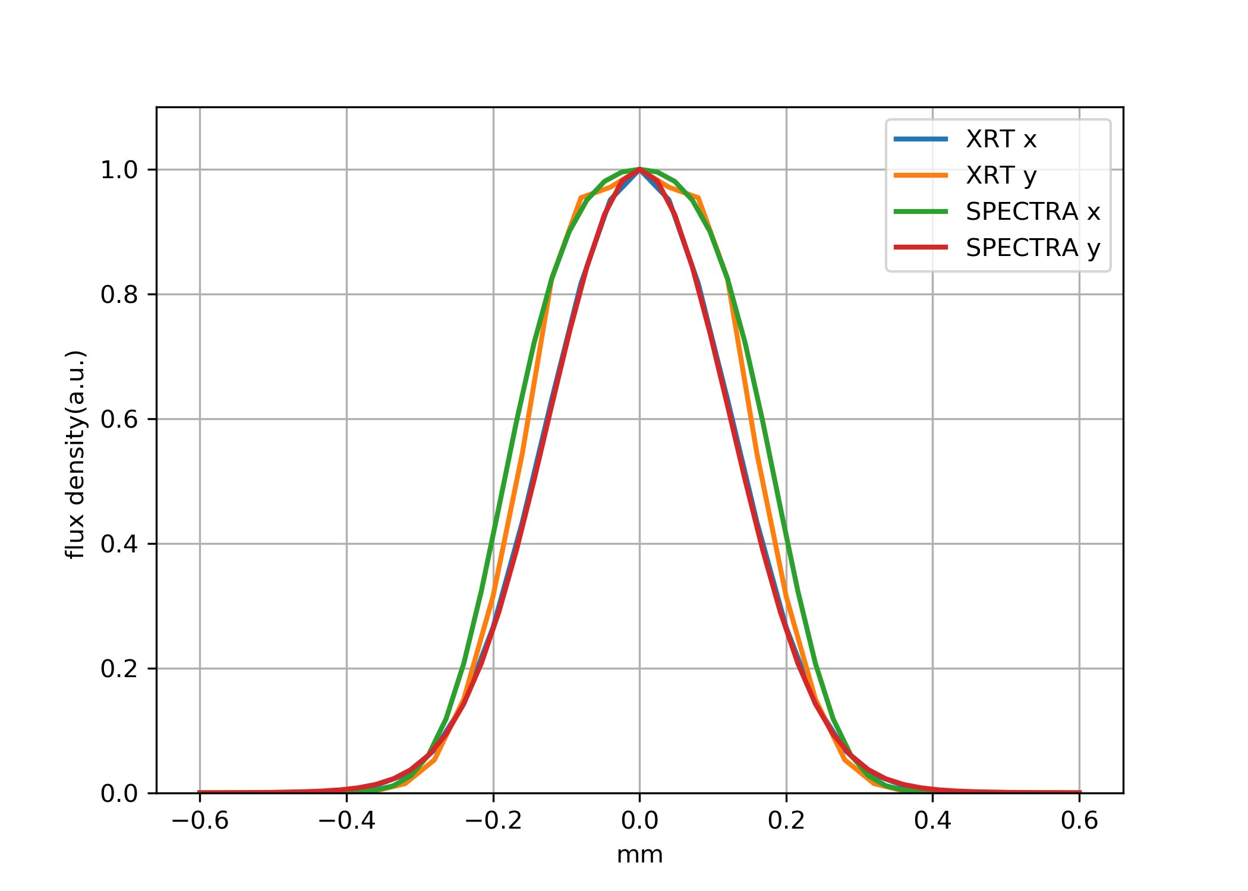
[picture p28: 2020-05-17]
design file/B1 beamline/compareTaper1.png

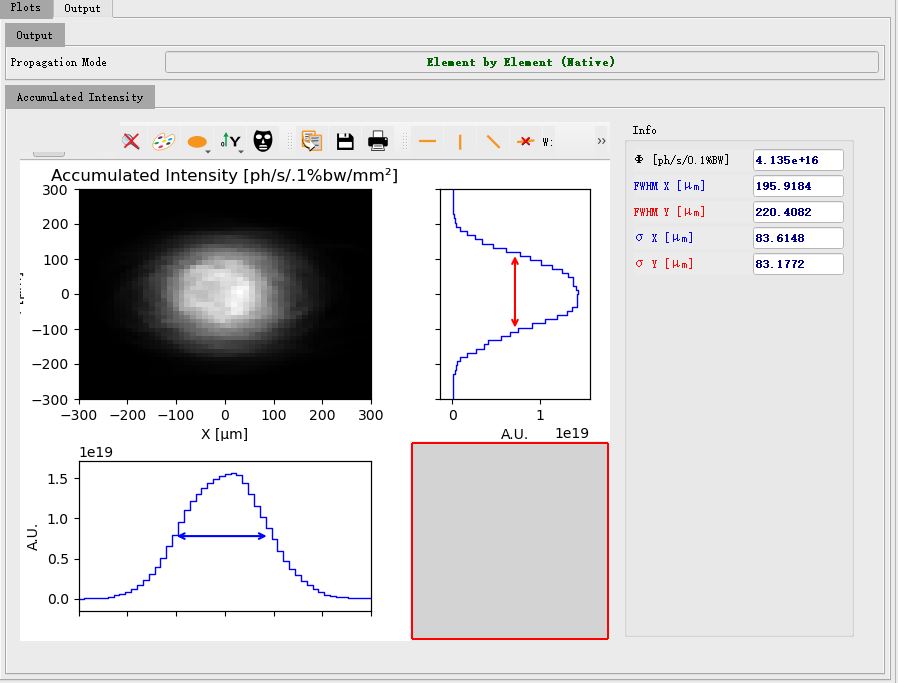
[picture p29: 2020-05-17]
design file/B1 beamline/SRW.JPG

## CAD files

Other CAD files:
Simulations/Radiation Shielding Design/tracing/2018.08.06 ID45 BR.dwg
Simulations/Radiation Shielding Design/tracing/2018.08.06 BM FE BR.dwg

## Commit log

2020-03-18 SRW画图
2020-03-19 SRW和XRT的波动计算复核
    SRW和XRT的波动计算复核1 – 光源发光特征的计算
2020-03-20 B8束线微米和亚微米聚焦模式的性能分析
    包括波动传播和几何追迹，为了提高分析效率，这里又分为单电子和多电子追迹的情况。
2020-03-22 标准格式修改
    参考MD文件的编辑方法，修改了文件内容的排版
2020-03-29 Create 31-35.玩转Linux操作系统.md
    学习linux操作
2020-03-31 Create 工作笔记20200331 - Taper模式计算.docx
2020-04-05 格式修改
    格式修改
2020-04-11 关于基底面形的考虑
    从束线设计需求、加工工艺、分析方法等方面，开展讨论。目标是确定HEPS的SPECIFICATION
2020-05-20 韧致辐射追迹计算
    [2018.08.06 BM FE BR.dwg, 2018.08.06 ID45 BR.dwg]
2020-05-27 修改V3
    准直器画图放在最终，外轮廓尺寸根据追迹计算结果确定
